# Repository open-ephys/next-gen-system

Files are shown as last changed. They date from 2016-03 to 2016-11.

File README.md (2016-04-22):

##  Next generation electrophysiology acquisition core
This repository is a work in progress repository for next generation open
source acquisition and closed-loop feedback system for multichannel
electrophysiology.

This project will hopefully end up being more than just an [open
ephys](http://www.open-ephys.org/) associated standard and will possibly be
moved to a different host org. Ideally we could end up with a set of open, and
evolving interface standards, code blocks and APIs that many different projects
can adapt parts of.

See the [working draft of the
specification](https://open-ephys.atlassian.net/wiki/display/OEW/PCIe+acquisition+board)
for details on the projects goals and desired features.

For now, we are aiming to build a working proof-of-principle prototype that we
can use as starting point to develop proper standards.

## License

### Hardware

<br/>
<span
    xmlns:dct="http://purl.org/dc/terms/" property="dct:title">Open Ephys FMC Intan IO module
</span> 
by 
<a xmlns:cc="http://creativecommons.org/ns#"
href="https://github.com/open-ephys/next-gen-system/" property="cc:attributionName"
rel="cc:attributionURL">Jonathan P. Newman, Jakob Voigts</a> 
is licensed under a
<a rel="license" href="http://creativecommons.org/licenses/by-sa/4.0/">Creative
Commons Attribution-ShareAlike 4.0 International
License</a>.
<br/>
Based on a work at <a xmlns:dct="http://purl.org/dc/terms/"
href="https://github.com/open-ephys/next-gen-system"
rel="dct:source">https://github.com/open-ephys/next-gen-system </a>

### Software
To be decided. Will likely be different licences for different layers of the
system (e.g. the firmware and devices drivers versus APIs and language bindings
versus plugins for various applications).

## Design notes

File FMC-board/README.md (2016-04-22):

# FMC Daughter Board

### Documentation

This board roughly conforms to the VITA 57 standard for LPC (low pin count) FMCs (FPGA Mezzanine Card).

It contains:
- 3x direct SMA connectors to the fpga, with overvoltage diode protection.
- 2x intan compatible 12pin omnetics connectors (A & B) for the intan headstage SPI standard, wired directly to the fpga, with a power supply.
- 1x isolated intan compatible connector (C) isolated through LVDS to CMOS converters and galvanic isolators. This headstage has its own power supply that is fed through am isolated DC-DC converter.
- 3x directional SMA connectors (on the card front edge) that are routed through the same isolation circuit as headstage connector C

The overall proposed architecture of the system is outlined [here](https://open-ephys.atlassian.net/wiki/display/OEW/PCIe+acquisition+board)

### Pinout
FMC LPC pinout can be found [here](https://docs.google.com/spreadsheets/d/18WfmbLGt8bGUUdksKp6AKA_wMX2SJ3Tndin-nnEgUCs/edit#gid=584734392)

### BOM
The bill of materials for this device can be found
[here](https://docs.google.com/spreadsheets/d/18WfmbLGt8bGUUdksKp6AKA_wMX2SJ3Tndin-nnEgUCs/edit?usp=sharing).

## Manufacturing requirements
- 4 layers
- 8mil trace width & spacing
- 12mil min. drill

There is one 0.05" pitch BGA connector (the samtech FMC connector) and a few omnetics connectors with inacessible pins on the board, so a stencil and reflow soldering need to be used.

The samtech FMC connector might need to be clamped or held down during reflow soldering. The samtec docs state that they should settle on their own during reflow though, so trying that first seems like a good idea (  http://suddendocs.samtec.com/processing/searay_soldering1.pdf ).

There is a round pad of kapton tape on the connector to provide a clamping surface for this purpose. We have had good success with using a steel paperclip that we modified to exert less force by cutting two slots into the spring. The original paper clips push down too hard and can warp the conenctor. Possibly just weighting it down with a suitable object could also work. Finally, the size of the connector means that it heats up pretty slowly, so expect it to reflow after everything else on the board, and if possible use proper pre-heating.

In order to meet approximately correct trace impedances, the design further is assuming:
 - 1oz copper
 - ~1.2mm total board height, ~0.25mm per layer, dielectric ER = 4.5

## TODO (Rev 1.0)
- [ ] Instead of conforming to VITA 57, PCB footprint should be made to fit in
  a PC expansion slot and be connected to the KC705 using a flex [FMC
  cable](http://suddendocs.samtec.com/prints/hdr-169472-xx-mkt.pdf). This will
  modularize the IO modules, potentially creating an ecosystem of different
  modules for different applications. It will also use extremely standardized
  interface (rear PC expansion slots) which also have excellent
  electrical/mechanical characteristics.
    - A couple interesting IO Module ideas
        - Analog module (e.g. NI DAQ replacement with some beefy multiplex SAR
          ADC and DAC on it)
        - Isolated Intan module (Similar to existing design, featuring galvanic
          isolation)
        - Adjustable logic level digital IO module
        - SPI compression module
        - Etc...
- [ ] As per [page 24 of the KC705 user
  guide](http://www.xilinx.com/support/documentation/boards_and_kits/kc705/ug810_KC705_Eval_Bd.pdf)
  we need to jumper the TDI and TDO pins of our FMC connectors to allow pass
  through of JTAG signals so the FPGA can be programmed when the FMC module is
  connected.
- [ ] For galvanically isolated IO module, we should conform to human use
  standards. Jakob has some info on what is required for this.

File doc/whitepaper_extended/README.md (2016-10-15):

# Open Instruments Whitepaper Extended version,

__Note:__ Contains interface specification overview and progress report.

## Overview

This whitepaper outlines an instrumentation system for neuroscience (and other
fields) that makes full use of existing technologies and industry standards to
deliver the ver high performance levels and modular design. The system can be
used as a platform for existing and future data sources, reducing development
overhead, while providing increases in system performance performance and
interoperability. This will also result in extendability to future interface
technology generations without the need for device specific re-engineering.

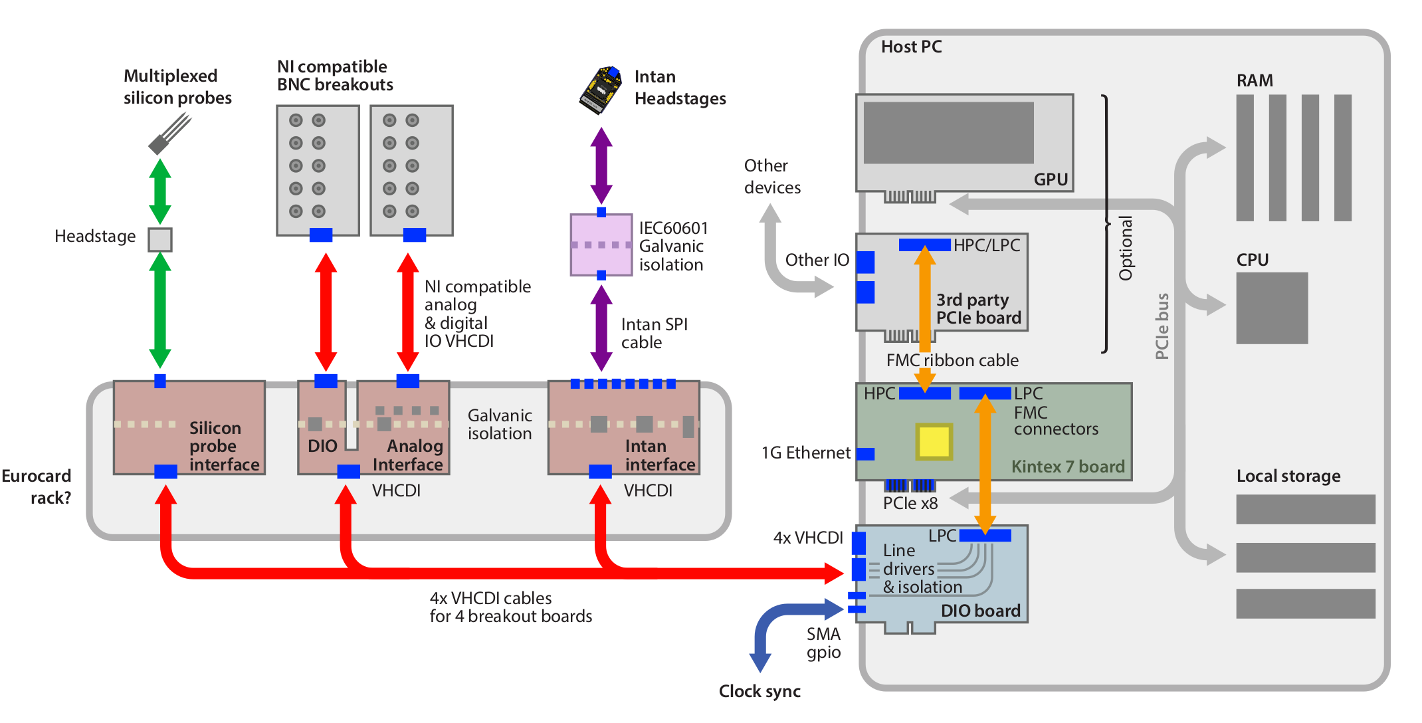
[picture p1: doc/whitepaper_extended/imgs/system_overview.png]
Example hardware configuration of a Open Instruments system with three connected breakout boards. In addition to the DIO board that provides the electrical connections between the FPGA and the breakout boards, a 3rd party FMC board is shown, connected to the FPGA through the second FMC connector.


_Example hardware configuration of a Open Instruments system with three
connected breakout boards. In addition to the DIO board that provides the
electrical connections between the FPGA and the breakout boards, a 3rd party
FMC board is shown, connected to the FPGA through the second FMC connector._

We have built a prototype system based on parts of these specifications that
delivers full use of the PCIe bus (12 Gbps throughput currently, up to 100 Gbps
with other FPGA boards). This provides adequate bandwidth for above 10,000
channels sampled at 30 kHz, and low latency of less than 100 μs round trip
between the host PC's main RAM allowing high level languages and libraries to
be used for closed-loop experiments. The same system potentially could also be
used for dynamic clamp applications using a real-time OS, delivering less than
10 μs loop capability.

The __Open Instruments__ standard does not specify or constrain the design of
either the data sources, nor the software used for data acquisition, but
specifies a flexible interconnect between the two. 

To implement a system based on new type of probe, only two or three components
need to be designed: 

  1. A hardware interface that connects directly to FPGA pins trough a
     standardized high-speed digital interconnect via generic 68-pin VHDCI
     connectors and cables that are connected to the FPGA boards via the
     ubiquitous FMC connectors and an intermediate DIO board as mechanical
     interconnect.
  1. A firmware module for the FPGA that drives this hardware, but does not
     need to be able to communicate with the host PC, or be developed with
     drivers in mind.
  1. (Optional) A software that communicates with this hardware through the
     open instruments AI that provides a generic interface to the hardware via
     data transfers and device registers, and can be used with no knowledge of
     the underlying interconnect (PCIe, USB, Ethernet).

By removing and standardizing the intermediate components of hardware-software
interfaces, the development effort required for this is vastly reduced, and
different data sources can be operated together in one system.

## Progress & Proof of Principle

The main design constraints behind this specification are high throughput and
low latency. In terms of throughput, most current interfaces can achieve or
exceed 10 Gbs. [PCIe](https://en.wikipedia.org/wiki/PCI_Express), which is used
as the basic for almost all other existing interfaces can currently achieve
around ~100 Gbs, which far exceeds the bandwidth required for any current or
mid-term electrophysiology applications, but could be useful eventually. By
contrast, latency varies widely across interfaces, and PCIe can achieve far
shorter closed-loop delays than any other mainstream interface for commodity
PCs.

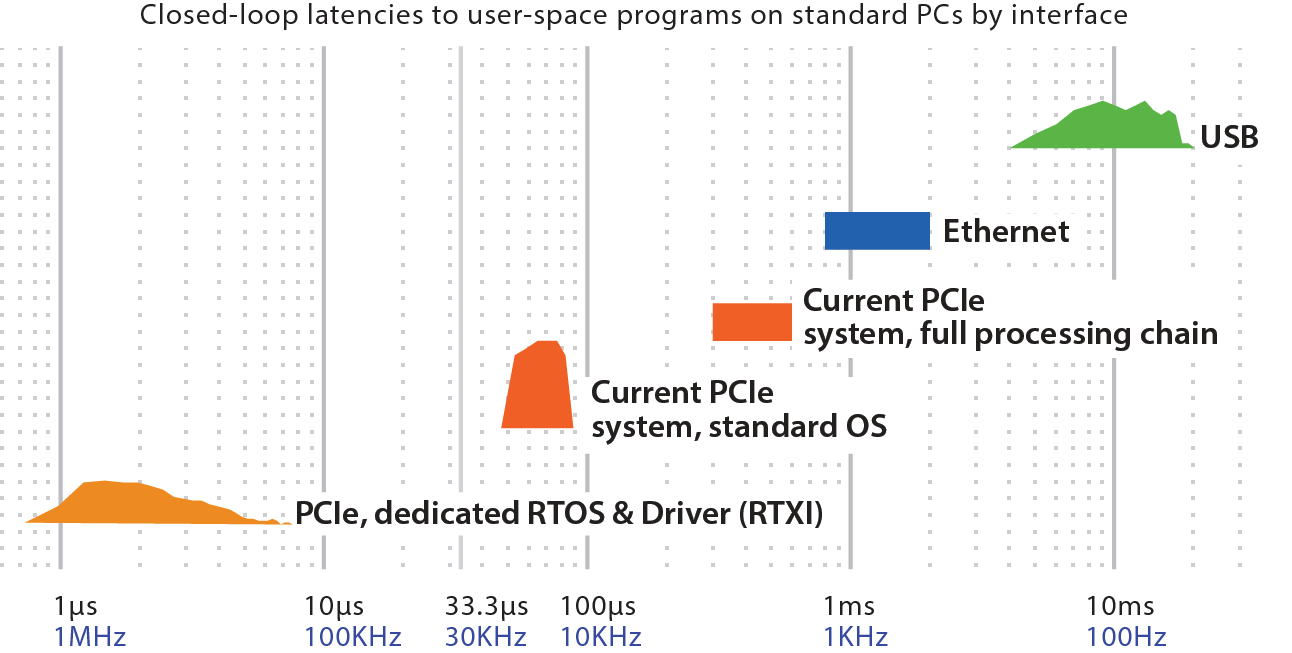
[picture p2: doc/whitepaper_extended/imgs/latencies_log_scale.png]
Overview of latencies across hardware interfaces. Histograms reflect measured latencies, bar plots reflect estimates.


_Overview of latencies across hardware interfaces. Histograms reflect measured
latencies, bar plots reflect estimates._

We have designed a prototype system based on a PCIe FPGA evaluation card
(latency measurements are shown above) and used it to verify the feasibility of
low-latency feedback on commodity PC hardware. 

In addition to verifying the feasibility of low-latency feedback via PCIe, we
tested the computational tractability of closed-loop experiments on a commodity
PC. By performing low-latency computations in a separate real-time thread, we
were able to detect spikes and perform significant additional computations on
each of 512 channels while reacting to spikes in less than 100 μs.

## Specification Overview

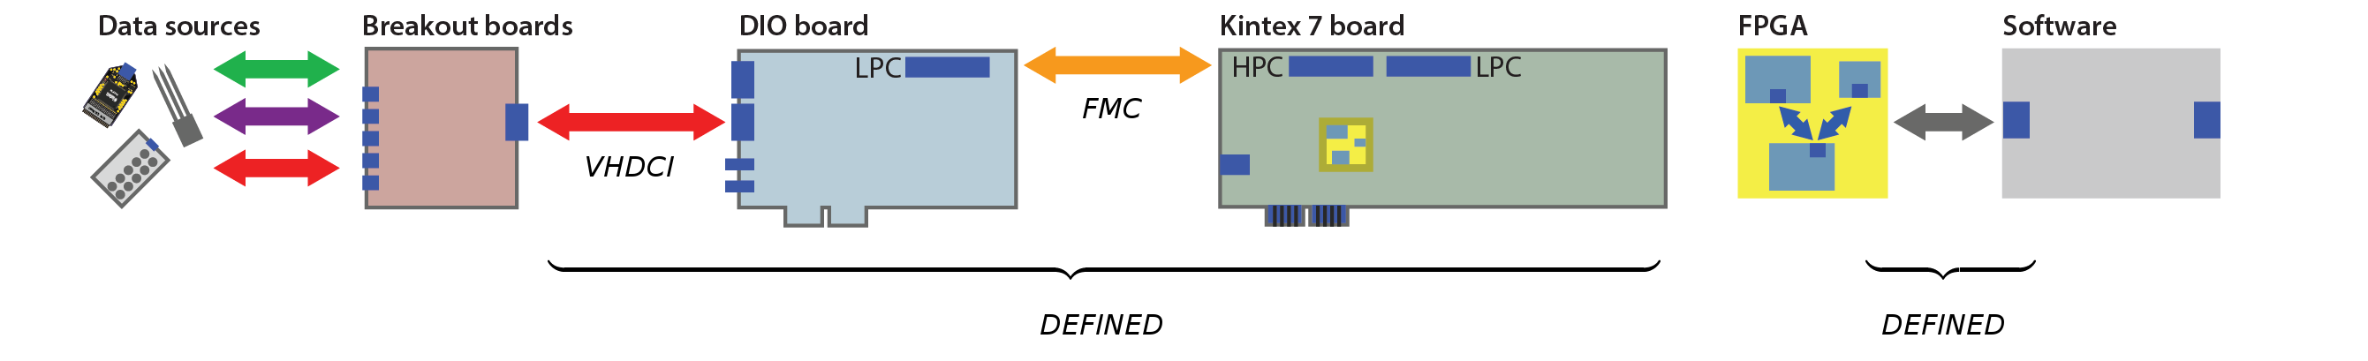
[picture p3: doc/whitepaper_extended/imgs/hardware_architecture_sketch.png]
Overview of the components and interfaces of the system. Only the interconnect infrastructure between the data source and the software are defined by the open instruments standard.


_Overview of the components and interfaces of the system. Only the interconnect
infrastructure between the data source and the software are defined by the open
instruments standard._

### Interface for Hardware Modules

This specification does not apply any constraints to the data source other than
the presence of a standardized VHDCI connector. This makes it possible for
almost any hardware to integrate into the system with minimal engineering
effort, and without sacrifices in performance.

Most pins on the cable are connected directly to the FPGA, arranged in the
following manner

  - 21 LVDS pairs that can be used in any way (including as 42 non-LVDS
    signals, depending on the device-specific firmware). 
  - 2 pins are dedicated to an I2C bus to obtain daughter board IO IDs and
    metadata,
  - 4 undefined pins for that can be used in any way
  - 20 Power supply pins (12 ground pins, 4 +5V pins, and 4 +12V pins) ground
    and VCC. 

See google [doc of pin out specification] (https://docs.google.com/spreadsheets/d/18WfmbLGt8bGUUdksKp6AKA_wMX2SJ3Tndin-nnEgUCs/edit#gid=438515320)

VHDCI cables are very widely available in low cost or very high quality
variants, and are very robust and rated for many cycles. Examples of hardware
modules are:

  - A simple Analog/Digital front-end with ADCs DACs and line receivers and
    drivers for digital input/output. This would also be the only piece of
    hardware needed to use the system in a dynamic clamp whole-cell experiment.
  - An interface to Intan headstages.
  - A digital interface connecting to high density CMOS probes.

### Hardware: DIO Card & FPGA Evaluation Card

There are only two hardware components of the system that are defined by this
specification:

  - An off-the shelf FPGA eval board (Kintex 7). This board hosts the FPGA that
    holds the device-specific firmware, as well as a piece of firmware that
    connects to the software, via the open instruments API. Exchanging this
    board for other FPGA carrier boards is relatively simple because we use
    industry standard FMC connectors to connect to the DIO board.
  - A very simple DIO card that directly connects pins on the FPGA to
    connnectors on the back of the host PC (via a FMC connector on the FPGA
    carrier board). The main role of this card is to provide direct electrical
    access to the pins of the FPGA. The FPGA pins on the FMC connector are
    broken out into 4 VHDCI connectors.

### Interfaces for Firmware Module

The open instruments standard does not specify the firmware / IP cores used to
interact with specific data sources. It does however provide a standardized
interface to a piece of firmware / IP core on the FPGA that provides a
flexible, bidirectional interconnect to the software. This minimizes
development efforts for new data sources by eliminating the redundant task of
driver and API development.

Examples of data source specific IP are:

  - An Analog/Digital IO driver that connects to a Analog/Digital front-end,
    handling the ADCs etc.
  - An Intan firmware IP core that replicates the existing Intan Rhythm
    firmware. 
  - A generic SPI interface module that can connect to data sources that
    already include an FPGA that can implement an SPI interconnect. This could
    for instance allow electrophysiology systems to be extended with very low
    latency capability.

### Software Interface

This specification does not impose any limitations on the software used to
operate the hardware modules, but specifies a very flexible interface by which
the software communicates with the hardware. This means that both the IP cores
and the software can be independent of the actual interconnect implementation.

Every communication between the software and the hardware can be cast as either
_(i)_ a read or write from/to a register (of arbitrary size) on the hardware,
for example for configurations, state read-outs etc. or _(ii)_ a read or write
from/to one of possibly many streams, for example for neural data or control
signal streaming.

The API also specifies how devices connected to the FPGA can be discovered and
identified by software, and keeps track of connection status.

## Next steps

Even though we have developed most of the specification and implemented a
working prototype system, there are a number of tasks that we will need to
complete in order to make the system practically functional and usable by other
developers:

  - Design and fabricate the DIO card to interface hardware modules to the
    FPGA.
  - We will also develop two very simple core hardware modules: An Intan
    amplifier chip interface identical to current basic intan systems, and an
    Analog/Digital front-end.
  - Implement the open instruments API around an existing PCIe firmware and
    driver, possibly using the existing xillybus driver as a short-term
    solution, and port some existing software packages (Bonsai, Open Ephys) to
    use the API to acquire neural data.
  - Implement the generic digital interconnect to commercial systems and
    implement some basic data streaming functionality.
  - We will need to move the PCIe interface to a firmware and driver that do not impose licensing restrictions. This is especially important for use of the system as component of commercial systems.

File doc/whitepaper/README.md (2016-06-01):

# Open Instruments Whitepaper

This whitepaper outlines an instrumentation system for neuroscience (and other fields) that makes full use of existing technologies and industry standards (PCIe and FMC connectors) to deliver the highest possible performance and modularity. The system can be used as a platform for any existing and future data sources, reducing development overhead, without imposing any performance or usability drawbacks. This also result in extendability to future interface technology generations without the need for device specific re-engineering.

Example hardware configuration of a Open Instruments system with three connected data source 'breakout boards'. In addition to the DIO board that provides direct electrical connections between the FPGA and the breakout boards, a 3rd party FMC board is shown, connected directly to the FPGA through t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

_Example hardware configuration of a Open Instruments system with three connected data source 'breakout boards'. In addition to the DIO board that provides direct electrical connections between the FPGA and the breakout boards, a 3rd party FMC board is shown, connected directly to the FPGA through the second FMC connector._

We have built a prototype of the system that delivers full use of the PCIe bus (12Gbps throughput currently, up to 100Gbps with other FPGA boards) for >10.000 channels sampled at 30kHz, and low latency of  <100μs round trip to and from the host PC, so that high level languages and libraries can be used for closed-loop experiments. The same system could also be used for dynamic clamp applications using a real-time OS, adding <10μs closed loop capability to existing and novel amplifier systems.

The open instruments standard does not specify or constrain the design of either the data sources, nor the software used for data acquisition, but specifies a flexible interconnect between the two. 

To implement a system based on a new type of data source, only two or three components need to be designed: 

(__1__) A hardware interface that connects to the data source and to FPGA pins on the open instruments board directly through a standardized high-speed digital interconnect via generic VHDCI connectors and via the ubiquitous FMC connectors and an intermediate DIO board as mechanical interconnect.

(__2__) A firmware module for the FPGA that drives the hardware (via any interface standard directly trough FPGA pins), but does not need to be able to interface with the host PC, or be developed with specific drivers in mind.

(__3__, optional) Data-source specific software that communicates with the hardware through the open instruments API which provides a generic interface to the hardware via data transfers and device registers, and can be used with no knowledge of the underlying interconnect (PCIe, USB, or Ethernet).

 By removing and standardizing the intermediate components of hardware-software interfaces, the development effort required for this is vastly reduced, and different data sources can be operated together in one system.

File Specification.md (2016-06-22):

# Open Instruments Specification

This specification defines interfaces for instrumentation systems for
neuroscience (and other fields) that makes full use of existing technologies
and industry standards to deliver the highest possible performance levels and
modular design. The system can be used as a platform for existing and future
data sources, reducing development overhead, while providing increases in
system performance and interoperability. The standard will also result in
extendability to future interface technology generations without the need for
device specific re-engineering.

For a brief overview, see the whitepaper at https://github.com/open-ephys/next-gen-system/tree/master/doc/whitepaper_extended

## Overview

An Open Instruments compatible system consists of one or more data sources or
effectors, termed 'daughter devices', that interact with software on a PC via
a series of standardized interfaces. The Open Instruments standard does not
specify or constrain the design of either the daughter devices, nor the software
used for data acquisition, but specifies a flexible interconnect between the
two.

Example hardware configuration of a Open Instruments system with threesd connected daughter devices / breakout boards. In addition to the DIO board that provides the electrical connections between the FPGA and the breakout boards, a 3rd party FMC board is shown, connected to the FPGA through the se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

_Example hardware configuration of a Open Instruments system with three
connected daughter devices / breakout boards. In addition to the DIO board that provides the
electrical connections between the FPGA and the breakout boards, a 3rd party FMC
board is shown, connected to the FPGA through the second FMC connector._

Examples of hardware modules / daughter devices  are:

  - A simple Analog/Digital front-end with ADCs DACs and line receivers and
drivers for digital input/output. This would also be the only piece of hardware
needed to use the system in a dynamic clamp whole-cell experiment. 

- A mostly passive interface to Intan headstages, with LVDS line interfaces,
- power supplies and galvanic isolators.

- A digital interface connecting to high density CMOS probes.

To add a new type of probe to an existing open instruments system, only two or three components
need to be designed:

  1. A hardware interface that connects directly to FPGA pins through a
  standardized high-speed digital interconnect via generic 68-pin VHDCI
  connectors and cables (which are connected to the FPGA boards via 
  FMC connectors and an intermediate DIO board as mechanical interconnect). 

  1. A firmware module / IP core for the FPGA that drives this hardware, but
  does not need to be able to communicate with the host PC, or be developed
  for specific drivers.

  1. (Optional) Software that communicates with this hardware through the open
  instruments AI that provides a generic interface to the hardware via data
  transfers and device registers, and can be used with no knowledge of the
  underlying interconnect (PCIe, USB, Ethernet).

By removing and standardizing the intermediate components of hardware-software
interfaces, the development effort required for this is vastly reduced. As an
added benefit, different data sources can be operated together seamlessly in
one system.

Overview of the components and interfaces of the system. Only the interconnect infrastructure between the data source and the software are defined by the open instruments standard.

_Overview of the components and interfaces of the system. Only the interconnect
infrastructure between the data source and the software are defined by the open
instruments standard._

#### Definitions

_Daughter device_ - Physical device / breakout bard that acts as a data source, or effector.

_Device type_ - unique id (enum specified in the API) that identifies daughter device types
and specifies the IP core, and device specific API that is used.

_Port_ - A VHDCI connector that connects a daughter device to the DIO board.

_DIO board_ - A PCIe format card that provides an electrical interconnect between
the FPGA and the daughter devices.

_FPGA board_ - A PCIe board that hosts the FPGA, as well as FMC connectors.

_FMC connector_ - A high pin count standardized connector for attaching devices to
FPGAs specified in the Vita 57 standard.

_IP core_ - A piece of firmware code that can be loaded to the FPGA.

_Open Instruments API_ - an API used by other software to communicate to
daughter devices via the FPGA.

_Device specific API_ - an API that uses the Open Instruments API to interact with a daughter device.

## Daughter device - FPGA interface

Daughter devices connect to the FPGA (which either controls the daughter device,
or simply provides an interface to the host PC) by a flexible interface that does
not constrain what devices can be used, but ensures future interoperability.

### Physical and signal type specification

Daughter devices connect to the FPGA via a very simple DIO card that directly
connects pins on the FPGA to connnectors on the back of the host PC via a FMC
connector on the FPGA carrier board.

The main role of this card is to provide direct electrical access to the pins of
the FPGA. The FPGA pins on the FMC connector are broken out into 4 VHDCI
connectors.

See https://docs.google.com/spreadsheets/d/18WfmbLGt8bGUUdksKp6AKA_wMX2SJ3Tndin-nnEgUCs/edit?usp=sharing 
for the full pin assignment.

Most pins on the cable are connected directly to the FPGA, arranged in the
following manner

  - 21 LVDS pairs that can be used in any way (including as 42 non-LVDS signals,
depending on the device-specific firmware).    

- 2 pins are dedicated to an I2C
bus to obtain daughter board IO IDs and metadata,   

- 4 undefined pins 
that can be used in any way   

- 20 Power supply pins (12 ground pins, 4 +5V
pins, and 4 +12V pins) ground and VCC.

VHDCI cables are very widely available at low cost or in very high quality
variants, and are very robust and rated for many mating cycles.

In addition to the VHDCI connectors, the DIO card also provides a few SMA connectors that can be used as clock IO to synchronize multiple systems.

_Possible later extension:_ The kc705 boards provide 4 GTX tranceivers (12Gbps
each) on the HPC FMC connector. Many other FPGA eval boards provide similar
high-speed pins. For a further expansion of the system, these pins could be
routed to external SPF or esata connector on the DIO board, providing a
significantly higher throughput option for device specific or generic digital interfaces.

### Protocol layer

The Open Instruments standard does not enforce any protocol - a daughter device
can communicate with the FPGA via the signal lines on the VHDCI connector
defined in the physical layer in any way. This includes the use of LVDS pins for
single ended signals.

The only specification, apart from the pin out, is the presence of an i2c EEPROM
(either as IC or emulated on a microcontroller or FPGA) on the daughter device
that identifies the device to the FPGA and determines what IP cores are
conencted to the device's port. This identifier is also available to software
via the API.

#### Canconical SPI protocol

If desired, a daughter device can choose to adhere to a simple standardized
protocol to stream data to and from the system via the VHDCI connector. To do
this, the device simply needs to identify (via the eeprom) as a 'canonical SPI
device'. From the point of view of the open instruments standard, this canonical
SPI protocol and the associated IP core are treated like any other daughter
device and device- specific IP core.

In this case, the canonical SPI IP core is connected to a subset of pins on the
VHDCI port.

2do: define this more.

## FPGA - host interface 

The Open Instruments standard opaquely encapsulates the FPGA/host interface so
that neither hardware, firmware nor software need to be modified significantly in
order to switch between interfaces. On the software side, the interface is
encapsulated by the Open Instruments API, and on the firmware side by the Host
interface IP core.

Overview of latencies across hardware interfaces. Histograms reflect measured latencies, bar plots reflect estimates.

_Overview of latencies across hardware interfaces. Histograms reflect measured
latencies, bar plots reflect estimates._

### Ethernet 

Ethernet interfaces combine low latency of ~1-5ms with high
troughput of around 10Gbps on common ethernet cards, which is sufficient for
almost all current applications.

The kc705 FPGA board includes a 10gig Ethernet connector, so implementing the
interconnect via ethernet will just require an appropriate IP core.

### PCIe

[PCIe](https://en.wikipedia.org/wiki/PCI_Express), which is used as the basic
for almost all other interfaces can currently achieve throughputs of around ~100
Gbts, which far exceeds the bandwidth required for any current or mid-term
electrophysiology applications, but could be useful eventually. The most common
type of FPGA evaluation board that is recommended for open einstruments systems,
the Xilinx Kintex kc705 achieves around 12Gbps, which is sufficient for almost
all current applications.

PCIe can achieve far shorter closed-loop delays than any other mainstream
interface for commodity PCs. PCIe can achieve < 100 μs closed-loop latencies on
common operating systems, and around 1 μs on real-time operating systems (for
example, in the RTXI project).

## IP core /firmware module interfaces

The open instruments standard does not specify the firmware / IP cores used to
interact with specific data sources. It does however provide a standardized
interface to a piece of firmware / IP core on the FPGA that provides a flexible,
bidirectional interconnect to the software. This minimizes development efforts
for new data sources by eliminating the redundant task of driver and API
development.

### Wishbone bus

Individual IP cores on the FPGA communicate via a standardized interconnect
based on the wishbone specification.

2do: specify this more - ideally the wishbone specifications should very closely
mirror the API, similarly to how xillybus and opalkelly have equivalent API
calls for register writes/reads/wires to registers, and pipes/streams to fifos.

### I2C EEPROM interface

Each daughter device must contain an EEPROM on the i2c bus of the VHDCI port
that identifies the daughter device to the system. The device is identified by a
simple device id that is specified by an enum (oiDeviceType) in the open
instruments API. New device types will be appended to this enum later.

The device type fullfils two roles:

1. Specify the type of daughter device specific IP core that is connected to the port that the device is connected to. In some cases, if the required IP core is not present on the FPGA, this could require a reconfiguration of the FPGA.

1. Allow the  API to enumerate the connected devices and their types, so that an appropriate device specific API/library can be loaded.

2do: specify details

### Interconnect matrix

Each daughter device connected to one of the ports needs to be routed to an
appropriate IP core.  This is accomplished by an interconnect matrix that pairs
the pins on the port (VHDCI connector, connected to the FPGA via the FMC
connector) to nets of the appropriate IP core.

This interconnect matrix is fullly transparent to both the daughter device and
the device specific IP core, and connects all pins on the VHDCI port to
corresponding nets on the device specific IP core.

2do: when is this done? on oiOpenPort()?

### Daughter device specific IP cores

Each daughter device specific IP core is specific to one device type, defined by
the device type id enum (oiDeviceType).

In some cases, multiple instances of these cores will be implemented on the
FPGA.  For instance multiple generic SPI interfaces will likely be used
simultaneously.

The presence of a matching IP core is checked by oiGetDeviceType, and the VHDCI
pins on the port are associated with the ip core in oiOpenPort. 

2do: is oiOpenPort the correct call to do this?
2do: do we want that device specific IP cores can be enumerated by the API via
an oiGetCoreType call? 

_One possible way this could work is that we loop over the oiGetNumPorts ports,
and call oiGetDeviceType, and run oiOpenPort immediately. The return code then
signals whether an ip core is present, or present and already associated with a
port etc. Now the software could try uploading a different firmware that
includes the required IP cores?_

Examples of daughter device specific IP cores are:

  - An Analog/Digital IO driver that connects to a Analog/Digital front-end,
handling the ADCs etc. 

- An Intan firmware IP core that replicates the existing
Intan Rhythm     firmware.    

- A generic SPI interface module that can connect
to data sources that already include an FPGA that can implement an SPI
interconnect. This could for instance allow electrophysiology systems to be
extended with very low latency capability.

### Host interface IP core

All communication to the API and to device specific and user-facing software is
encapsulated on the firmware side into host interface IP cores that adhere to
the same wishbone interface as daughter device specific IP cores.

There are two types of interfaces by which the host  interface IP core
communicates with device specific IP cores: Registers, and streams.

Registers are accessed on the API via oiReadConfig and oiWriteConfig by simple
key/value (int) pairs. On the IP core, the configuration corresponds directly to
a register bank.

Ports can contain multiple streams, and each streams is accessed by oiReadStream
or oiWriteStream. On the IP core, these streams correspond to FIFOs.

2do: wrap this in a wishbone compatible interface.

Examples of host interface IP cores are:

- Ethernet

- PCIe via xillybus

## Software

The software comonents of a Open Instruments system can be divided into four
layers: Interface specific drivers, the Open Instruments API, the daughter device specific
libraries/APIs, and the user-facing software. Only the Open Instruments API is
specified by this standard and ensures interoperability between system
components. However, in almost all practical implementations, a driver (for
example for Ethernet, or PCIe) will already be present, so developers aiming to
integrate a new device only have to implement the device specific API and
possiby user-facing software.

Conversely, switching out the host PC interface should not require changes to the device specific code.

### Drivers

Drivers for the hardware-software interconnect are opaquely wrapped into the
open instruments API on one end, and the (wishbone bus compatible)
specification of the host- pc interface IP core on the other. This means that
developers can either develop for daughter devices without having to spend
time on the interconnect specifics, or swap interconnects without requiring
re-enginering of other system components.

Examples of interconnect drivers are:

- Ethernet driver, 

- xillybus.

2do: _possible exception to the independence of drivre/interconnect implementation_: 
it seems likely that we want to be able to (optionally)
configure the interconnect - for instance selecting block transfer sizes for a
speed thourghput tradeoff. We could specify that this is optional and of course
not driver independent, but that all API implementations should come with
default values so that no specific configuration is strictly required. Maybe
oiSetStreamAttributes already covers this? Or could there be other configuration
options that are needed in special cases?

### API

This specification does not impose any limitations on the software used to
operate the hardware modules, but specifies a very flexible interface by which
the software communicates with the hardware. This means that both the IP cores
and the software can be independent of the actual interconnect implementation.

The full API specification is found at https://github.com/open-ephys/next-gen-system/tree/master/API

Every communication between the software and the hardware can be cast as either
_(i)_ a read or write from/to a register (of arbitrary size) on the hardware,
for example for configurations, state read-outs etc. or _(ii)_ a read or write
from/to one of possibly many streams, for example for neural data or control
signal streaming.

The API also specifies how devices connected to the FPGA can be discovered and
identified by software, and keeps track of connection status.

### Daughter device specific APIs

On top of the Open Instruments API, there will be daugher-device specific functions that should not be implemented by the user-facing software
Examples of these are cable lenght calculation for the SPI bus on Intan chips, Impedance measurements, unpacking of data formats to interpretable values and timestamps, etc.

For this, a user facing software can use oiGetDeviceType to determine the correct device specific API to interact (via the Open Instruments API) with the hardware/firmware of that device.

### User-facing software

The User-facing software can either interact with the duagher device firmware directly trough the Open Instruments API, and/or an intermediate layer of a daughter device specific API.

Examples of user-facing software packages are:

- Minimalistic Open instruments data stream interface

- The Open Ephys GUI 

- Bonsai

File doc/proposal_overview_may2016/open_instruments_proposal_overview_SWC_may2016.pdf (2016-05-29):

# Next generation electrophysiology

# Interface standard proposal for very high data rate neurophysiology and low latency closed-loop experiments

SWC Workshop Next Gen (Open) Ephys: Hardware and Software May 25-26th 2016, London

## Requirements

> 1000 channels | NeuroPix, Neuroseeker, Miniscope, etc. ~10 Gbps, more later
< 1ms latency | Closed loop experiments, whole cell, etc.

## Ideally also

## Dynamic clamp capable: < 100μs closed loop latency to user sw

## Future proof, modular, not reliant on vendor specific components

# What design choices result from this?

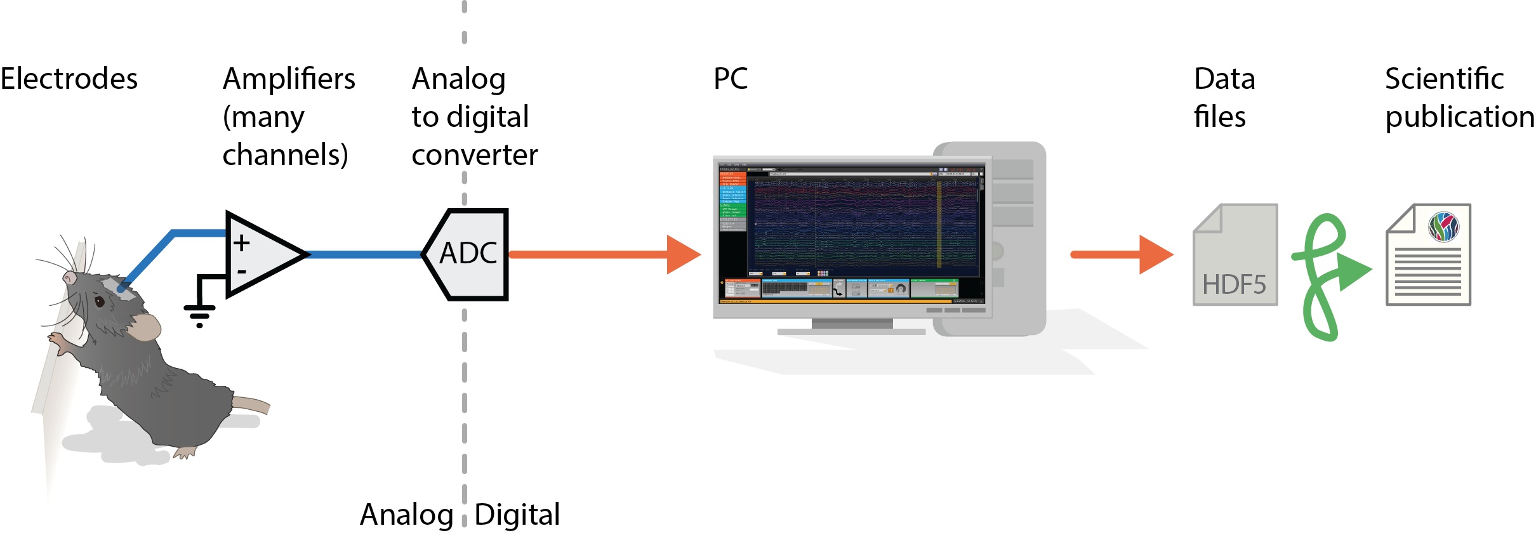
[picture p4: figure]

# Host PC interface

USB | High throughput, | High latency
| ~ 12 Gbps | ~ 15 ms
Ethernet High throughput, | Low latency
| ~12 Gbps | ~ 1ms
PCIe | Highest throughput, | Lowest latency
| ~12 Gbps (Max. ~100) | ~ 10 μs

# proof of principle: PCIe prototype

Direct PCIe DMA interface

> 1000 channels @ 30KHz
(approx. max. throughput is
25000 ch. * 16 bit * 30kHz = 12 Gb/s = 1.5 GB/s
Fills 1TB in ~11 minutes)

Aaron:
Direct port of Reid's Rhythm firmware & API via Xillybus

Jon & Jakob:
Simple FMC test board
1 isolated intan SPI connector,
1 non-isolated

3 isolated DIO (1 out, 2 in)
3 direct DIO (bidirectional)

Kintex 7 eval
PCIe 2 x4, $1600

FMC connector

# proof of principle: PCIe prototype

Kintex 7 eval
PCIe 2 x4, $1600

Intan

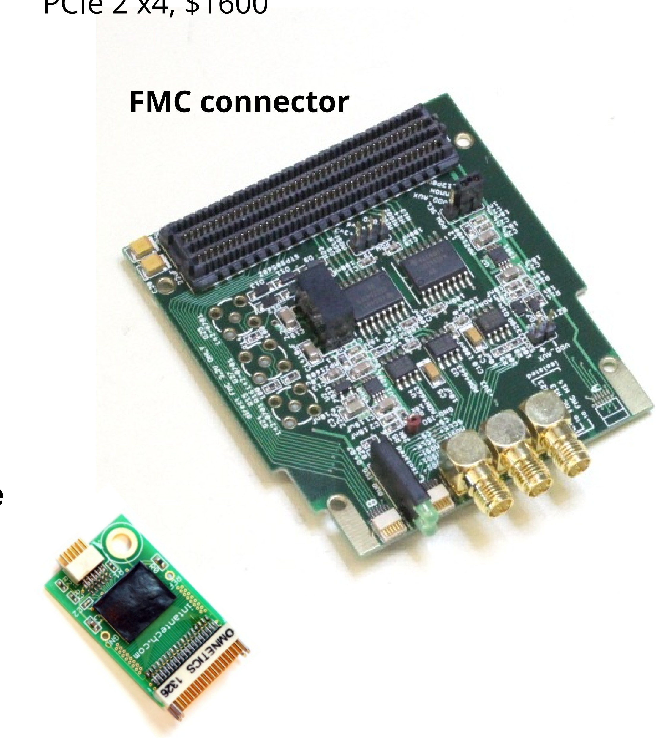
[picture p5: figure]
FMC connector

Headstage

Direct PCIe DMA interface

> 1000 channels @ 30KHz
(approx. max. throughput is
25000 ch. * 16 bit * 30kHz = 12 Gb/s = 1.5 GB/s
Fills 1TB in ~11 minutes)

Aaron:
Direct port of Reid's Rhythm firmware & API via Xillybus

Jon & Jakob:
Simple FMC test board
1 isolated intan SPI connector,
1 non-isolated

3 isolated DIO (1 out, 2 in)
3 direct DIO (bidirectional)

# PCIe prototype

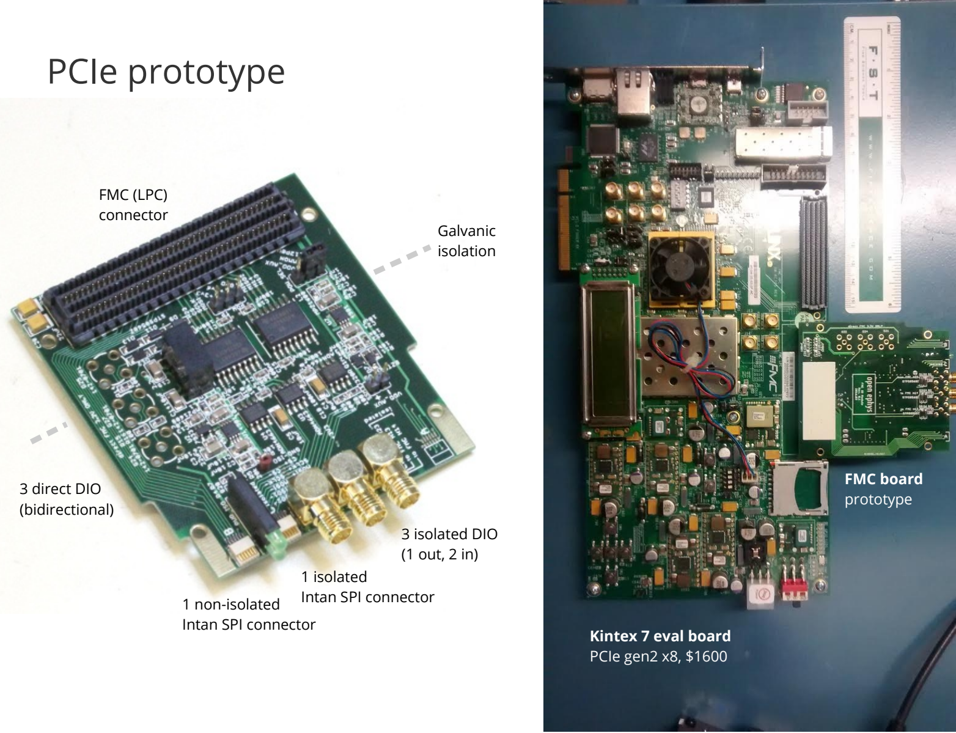
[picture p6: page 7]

Kintex 7 eval board
PCIe gen2 x8, $1600

Galvanic
isolation

3 isolated DIO
(1 out, 2 in)

3 direct DIO
(bidirectional)

1 isolated
Intan SPI connector

FMC (LPC)
connector

1 non-isolated
Intan SPI connector

FMC board
prototype

# Latency test

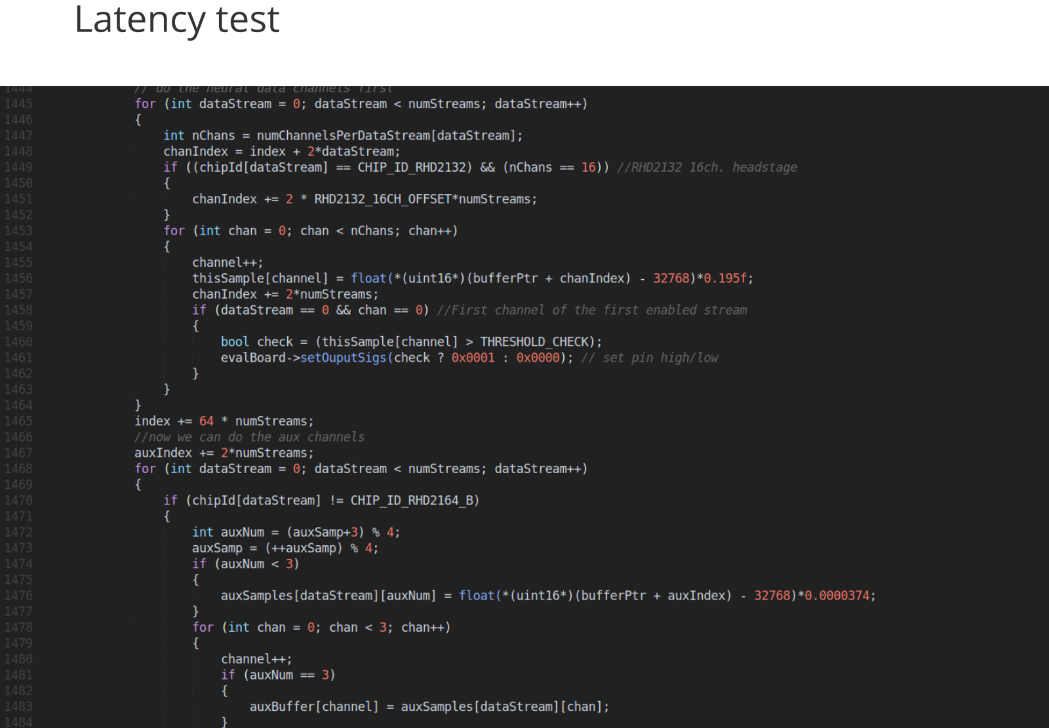
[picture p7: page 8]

# Latency test

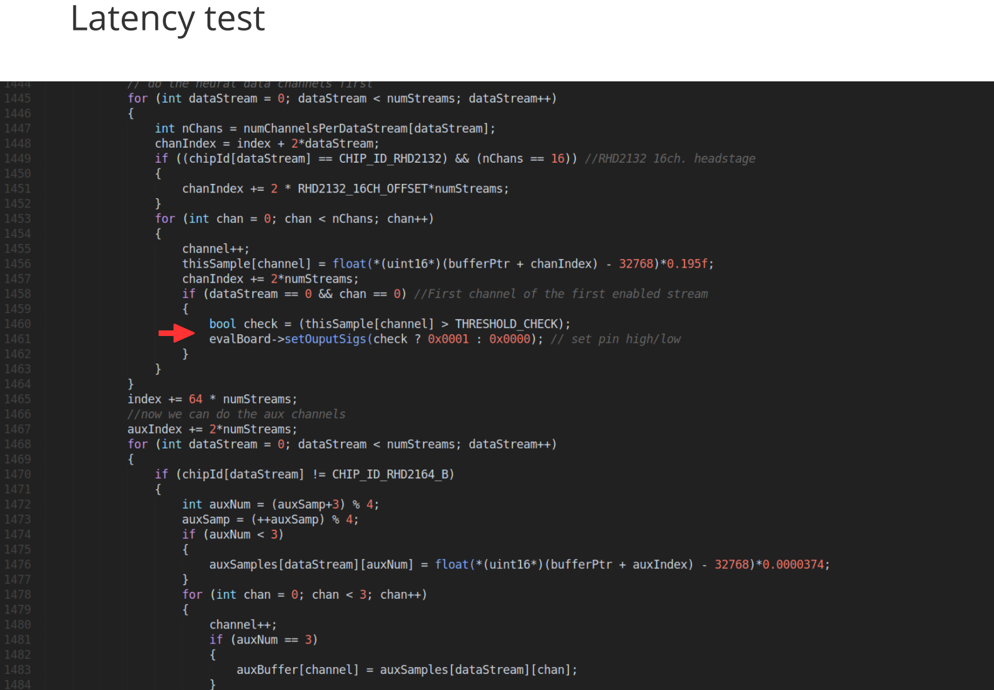
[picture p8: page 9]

# Latency test

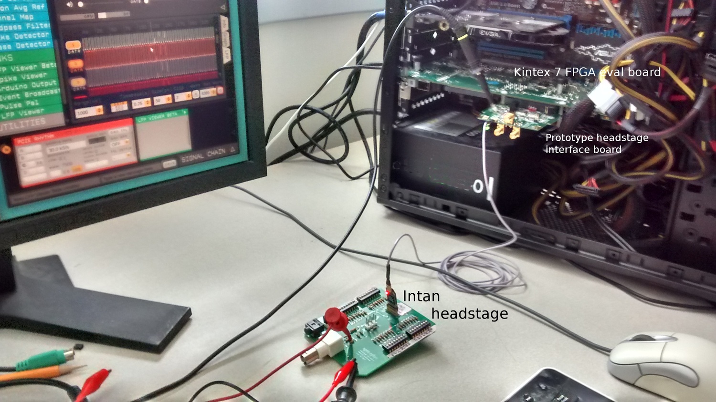
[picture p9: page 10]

# Latency results

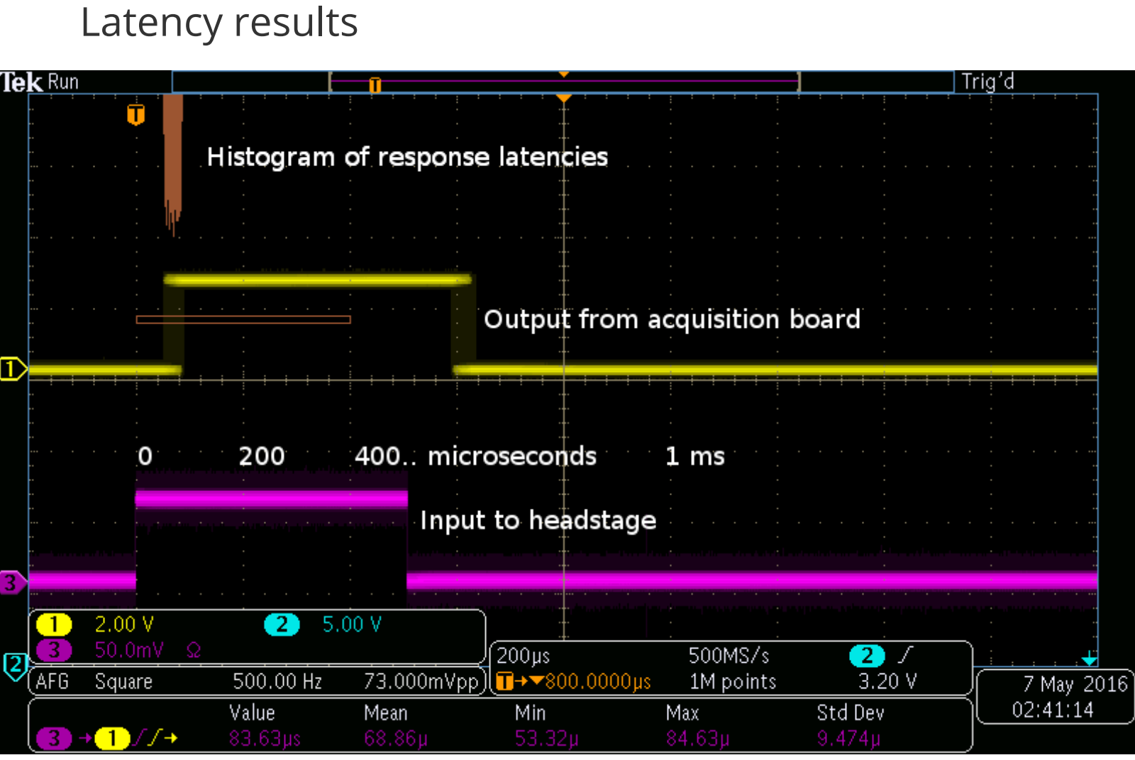
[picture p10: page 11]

# Latency results

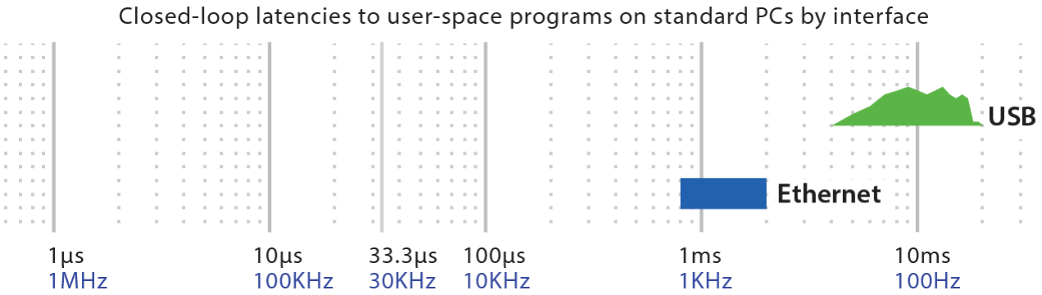
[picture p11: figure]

# Latency results

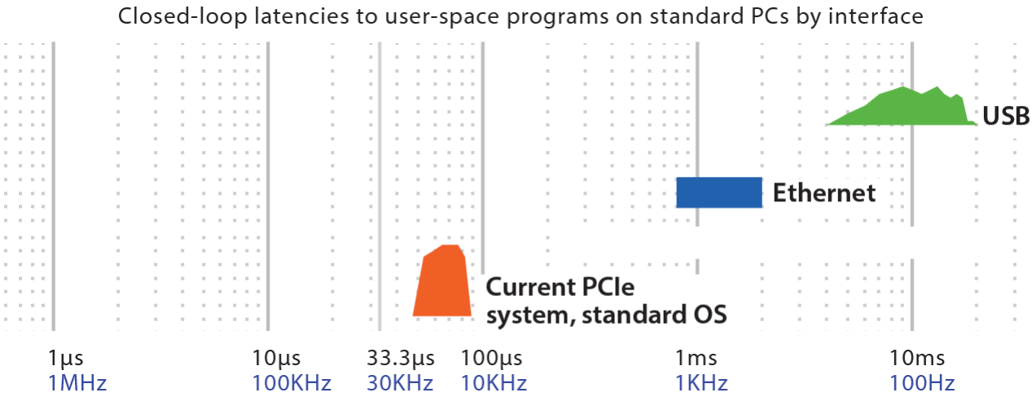
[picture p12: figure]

# Latency results

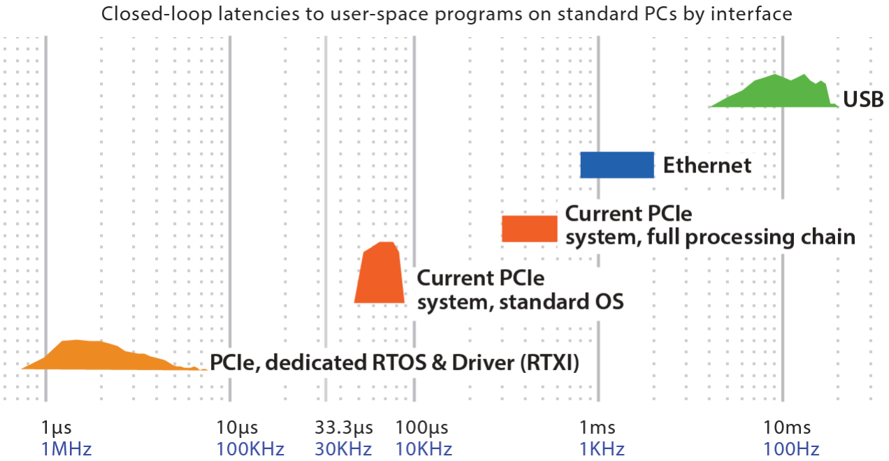
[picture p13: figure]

→ PCIe is sufficiently easy to implement,
Provides μs latency, at almost arbitrary channel counts.

# Which FPGA/PCIe card?

→ PCIe is sufficiently easy to implement,
Provides μs latency, at almost arbitrary channel counts.

# PCIe (FMC) carrier cards are already the industry standard

for similar applications.

Zynq board
ARM cortex integration

Kintex 7 eval

PCIe 2.0 x4, $1600 | HTG-828
| PCIe 3.0 x16

Cern FMC carrier
Open source design

Vadatech VPX514
VPX (VITA-46) card
(not strictly pure PCIe)

Stratix V dev kit.
PCIe 3.0 x16, dual FPGA, $15000

→ PCIe is sufficiently easy to implement,
Provides μs latency, at almost arbitrary channel counts.

# PCIe (FMC) carrier cards are already the industry standard

for similar applications.

Zynq board
Arm cortex integration

Kintex 7 eval

PCIe 2.0 x4, $1600 | HTG-828
| PCIe 3.0 x16

Cern FMC carrier
Open source design

Vadatech VPX514
VPX (VITA-46) card
(not strictly pure PCIe)

Stratix V dev kit.
PCIe 3.0 x16, dual FPGA, $15000

# Design choices for PCIe systems

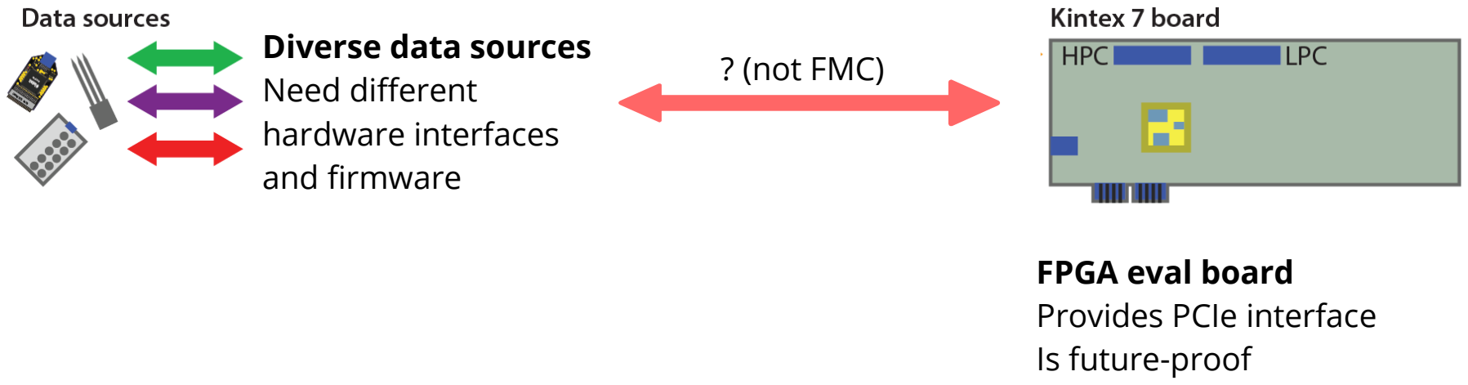
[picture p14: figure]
FPGA eval board Provides PCIe interface Is future-proof; Diverse data sources Need different hardware interfaces and firmware; ? (not FMC)

# Design choices for PCIe systems

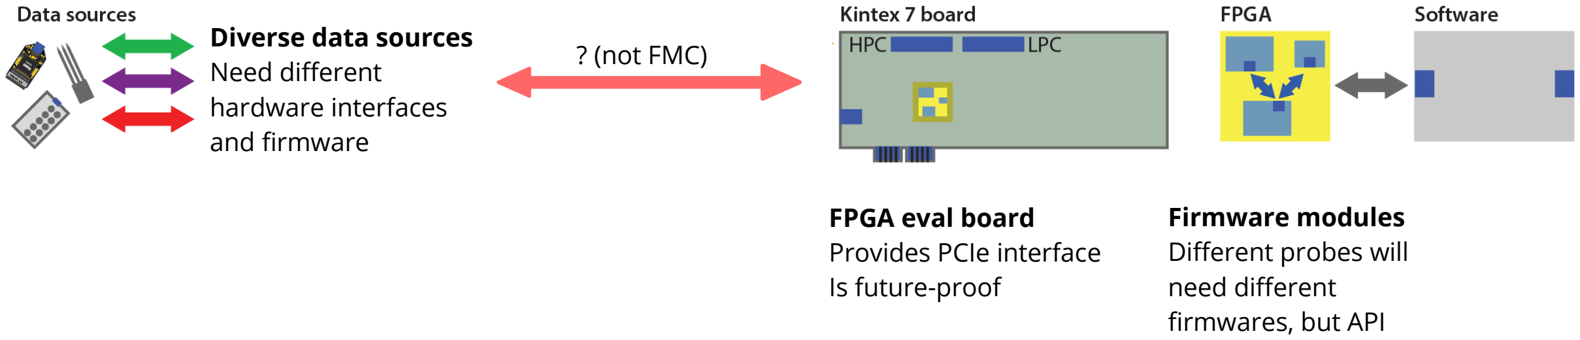
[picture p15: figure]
FPGA eval board Provides PCIe interface Is future-proof; Firmware modules Different probes will need different firmwares, but API; Diverse data sources Need different hardware interfaces and firmware; ? (not FMC)

interface can stay the
same.

# Design choices for PCIe systems

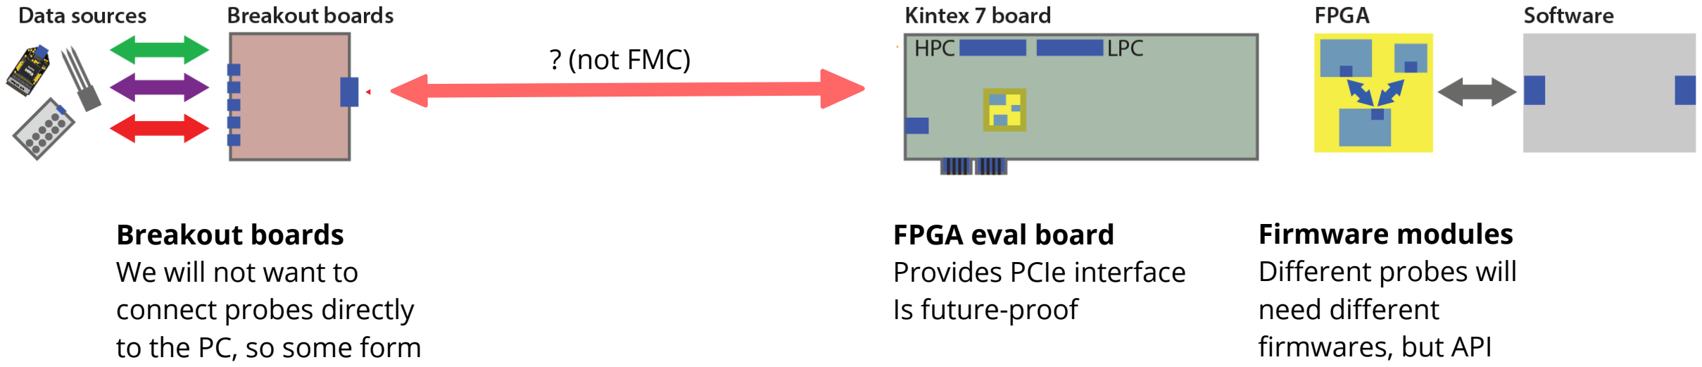
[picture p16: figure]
FPGA eval board Provides PCIe interface Is future-proof; Breakout boards We will not want to connect probes directly; Firmware modules Different probes will need different firmwares, but API; ? (not FMC)

to the PC, so some form
of breakout boards will
be needed.

interface can stay the
same.

# Design choices for PCIe systems

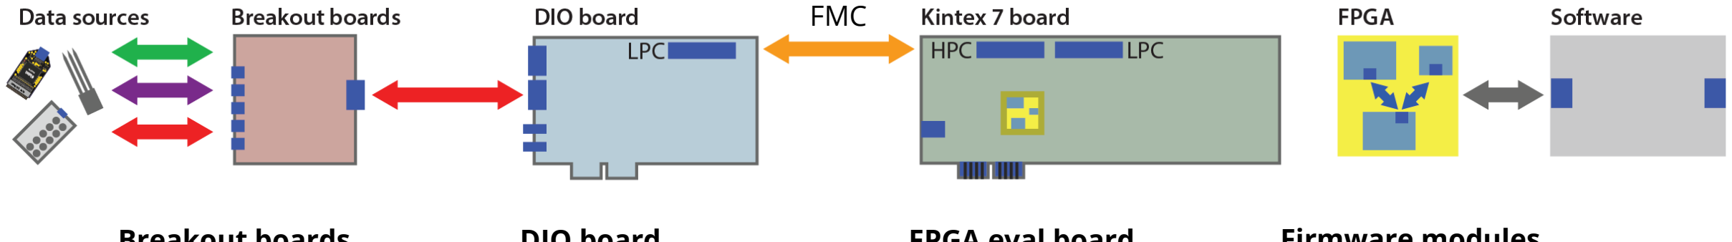
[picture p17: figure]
FMC

FPGA eval board
Provides PCIe interface
Is future-proof

Breakout boards
We will not want to
connect probes directly
to the PC, so some form
of breakout boards will
be needed.

Not always needed?

DIO board
Intermediate board
between FPGA board
and breakout boards.
FMC is great but not
useful for routing
outside PC case.

Firmware modules
Different probes will
need different
firmwares, but API
interface can stay the
same.

# Design choices for PCIe systems

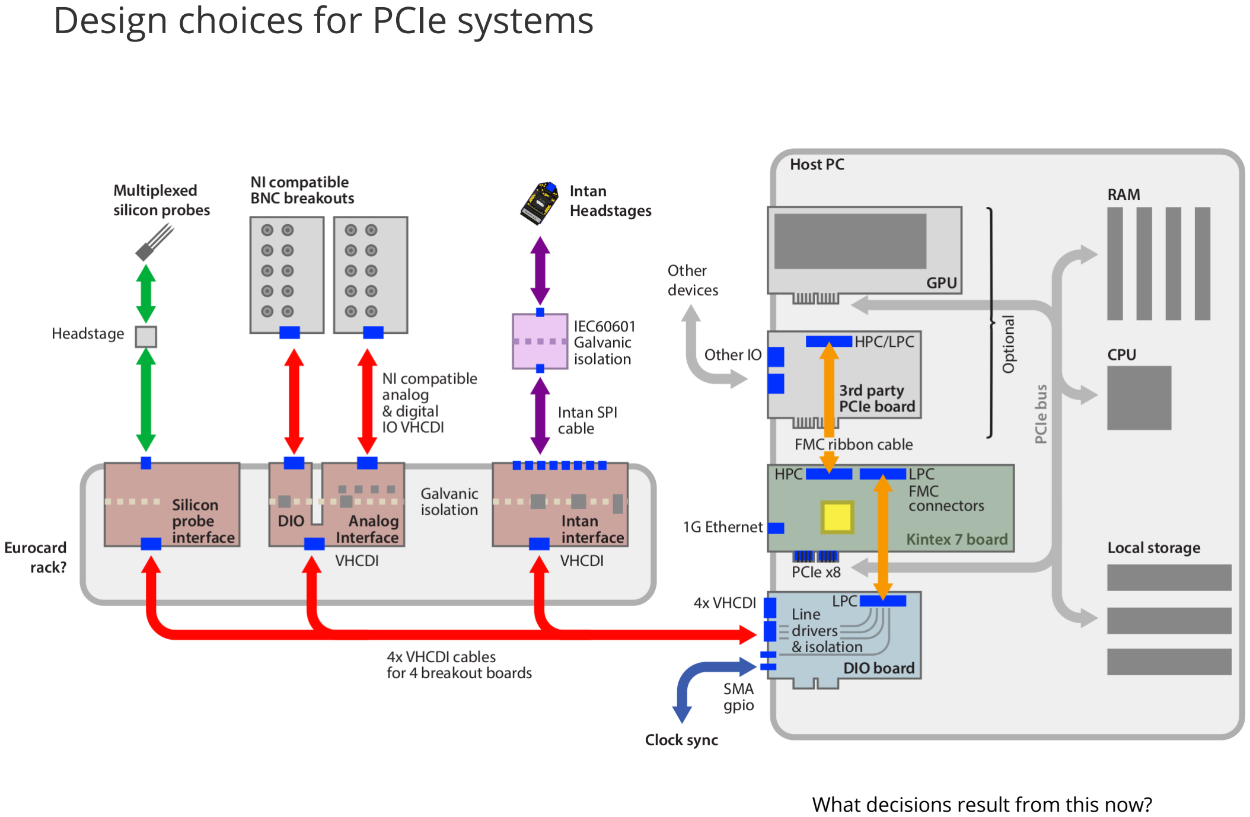
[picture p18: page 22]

What decisions result from this now?

# Design choices for PCIe systems FMC connector

To non-standard
board (microscopes etc.)

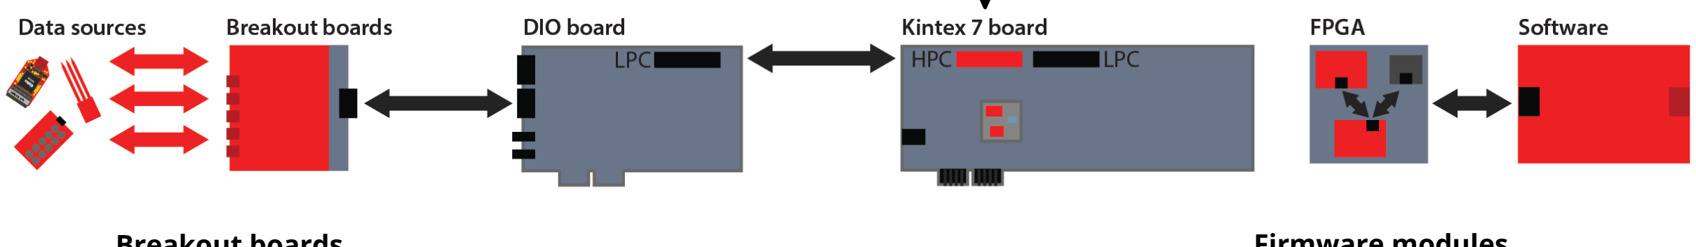
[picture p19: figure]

Breakout boards
Implement different
HW interfaces.

Firmware modules
Different probes will
need different
firmwares, but API
interface can stay the
same.

custom
standardized

# Design choices for PCIe systems

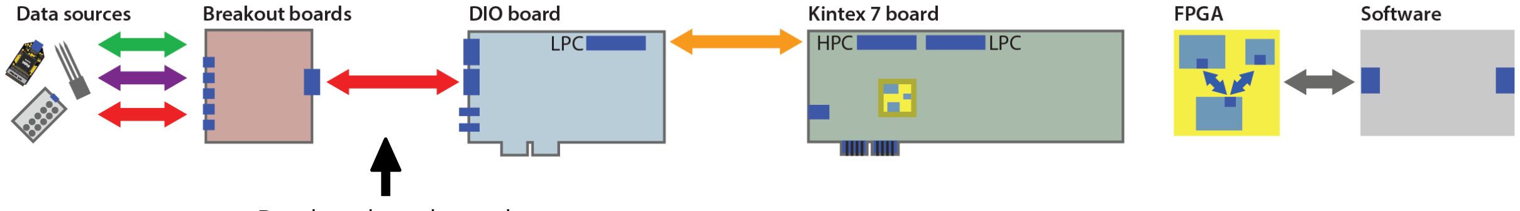
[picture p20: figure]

Breakout boards need to
connect to PC
Which connectors/cables?

# Design choices for PCIe systems

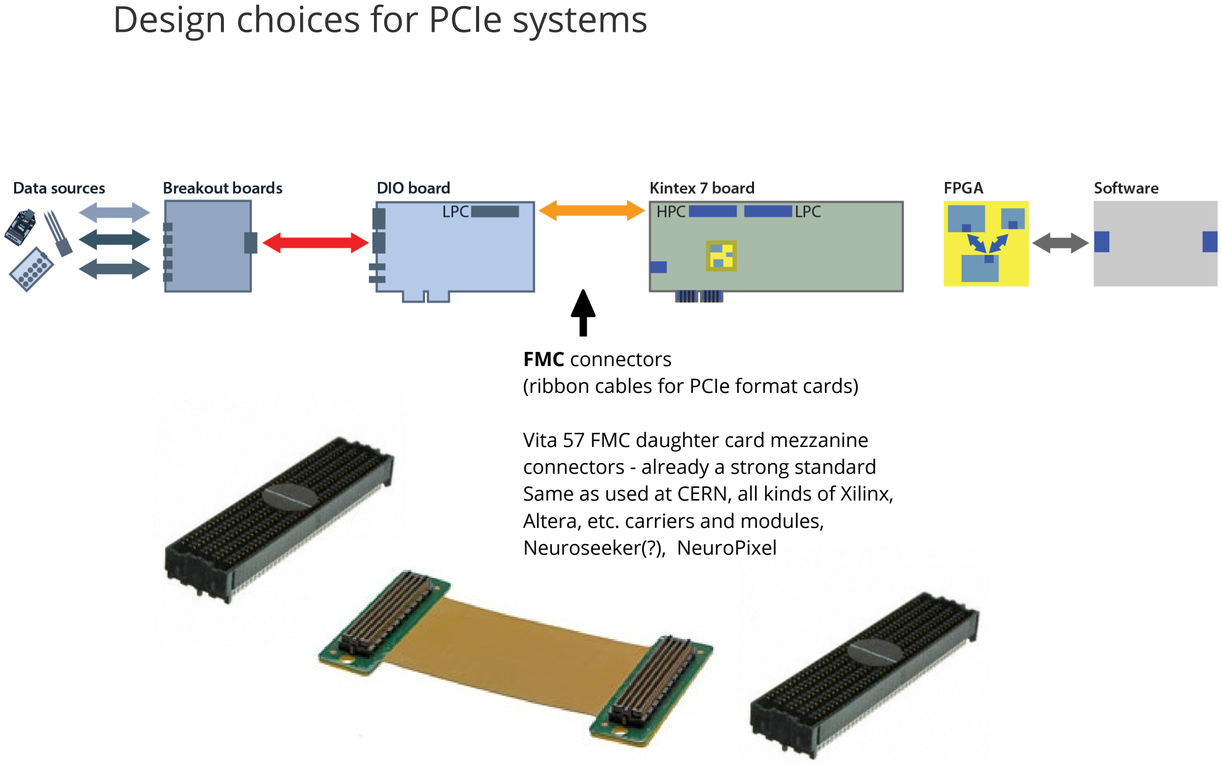
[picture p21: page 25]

FMC connectors
(ribbon cables for PCIe format cards)

Vita 57 FMC daughter card mezzanine connectors - already a strong standard Same as used at CERN, all kinds of Xilinx, Altera, etc. carriers and modules, Neuroseeker(?), NeuroPixel

# Design choices for PCIe systems

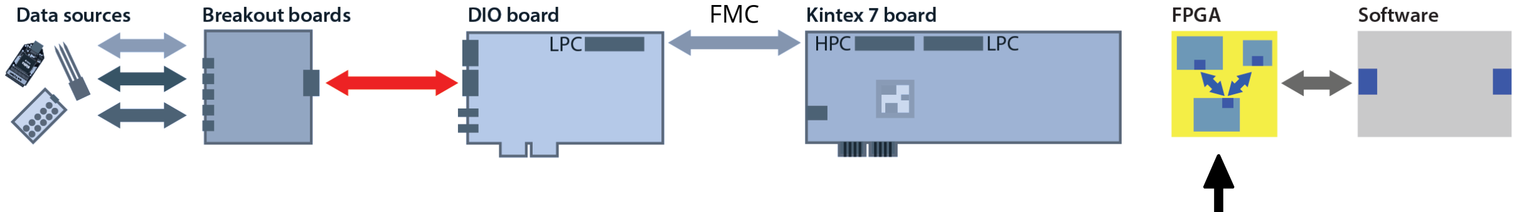
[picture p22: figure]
FMC

Firmware interconnect
Wishbone
IP cores?

# Design choices for PCIe systems

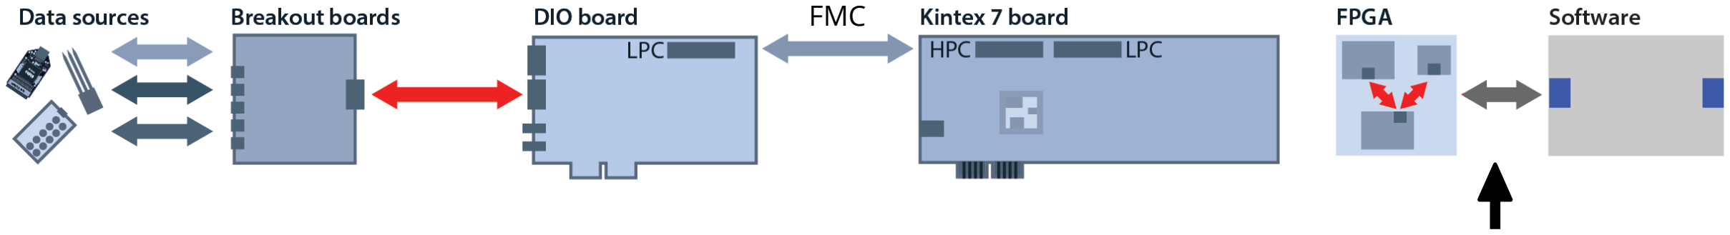
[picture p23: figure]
FMC

Host interface
PCIe (which method?)
optional Ethernet ?

# Design choices for PCIe systems

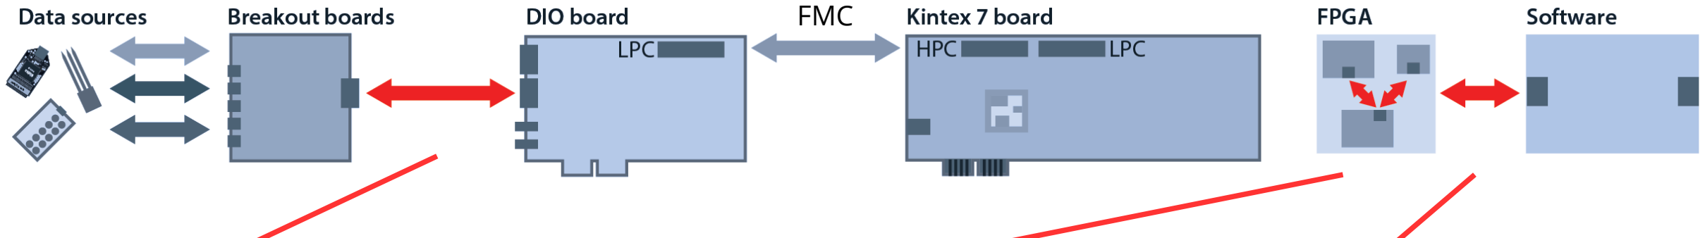
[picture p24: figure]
FMC

### 1. Breakout board

connectors

2. Firmware interconnect | 3. Host interface

# Design choices for PCIe systems


### 1. Breakout board

connectors

Just break out raw FMC pins VHCDI / SCSI cables

### 2. Firmware interconnect

Wishbone based
specification?

### 3. Host interface

Extendable PCIe based DMA
Plus ethernet for broadcast

# Breakout board connectors


Breakout board connectors

Just break out raw FMC pins to VHCDI / SCSI cables

Space for 4 conectors
& ~3 SMAs for clock etc.

68 pins
Twisted pairs
$25 - $400 options (shielded or not etc.) ~28GA ~600mA/wire →

Specify minimum number of pins
- VCC ( 3.3V & 12V ) /GND
- i2c bus for eeprom device id

Use LPC or HPC? Likely HPC since we want a decent pin count per connector.

# Breakout board format


Common use cases will employ 2-3 external breakout boards, likely double width, but there are cases for many more.

Eurocard format?

Don't use backplane, just use VHCDI? Can still use extruded aluminum case.

# Breakout board format

Common use cases will employ 2-3 external breakout boards, likely double width, but there are cases for many more.

Eurocard format?

Don't use backplane, just use VHCDI? Can still use extruded aluminum case.

Core application:
Data source Firmware
Aux input (A/D io)
PCIe interface

# IP core interfaces

Analog frontend

Intan headstages

# IP core interfaces

Extended application:
Data source Firmware
Aux input (A/D io)
PCIe interface
FPGA processing
Ethernet streaming

Analog frontend

Intan headstages

File storage server

# IP core interfaces

Interface between modules
Wishbone, which
specifications?

# IP core interfaces

Interface between modules
Wishbone interconnect?

Data format and config
register access is specified very similarly to the API.

# IP core interfaces

Host PC interface
Firmware side & Drivers

Currently use xillybus
Move to something with non-restrictive driver that can be used commercially.

# Conclusion

PCIe DMA interface is
- sufficiently developer friendly
- highest performance
- most future-proof

Proposed system can mostly use generic industry standards

Maintains compatibility with almost all existing standards

Minimizes amount of work
required for new data sources to close to theoretical minimum.

Interface specifications:
1. Breakout board standards
2. IP interconnect
3. PCIe PC interconnect ↔

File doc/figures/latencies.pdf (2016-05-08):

PCIe with very inecient but exible signal chain; Fully optimized PCIe (RTXI); Best case Ethernet; Ethernet; PCIe; PCIe on standard OS; USB 2/3; 10KHz; 1KHz

Latencies (μs) Corresponding frequencies

1KHz

100Hz

1MHz; 100KHz; 30KHz 10KHz; 1KHz; PCIe, dedicated RTOS & Driver (RTXI); Current PCIe system, standard OS; Current PCIe system, full processing chain; Ethernet; USB

Closed-loop latencies to user-space programs on standard PCs by interface

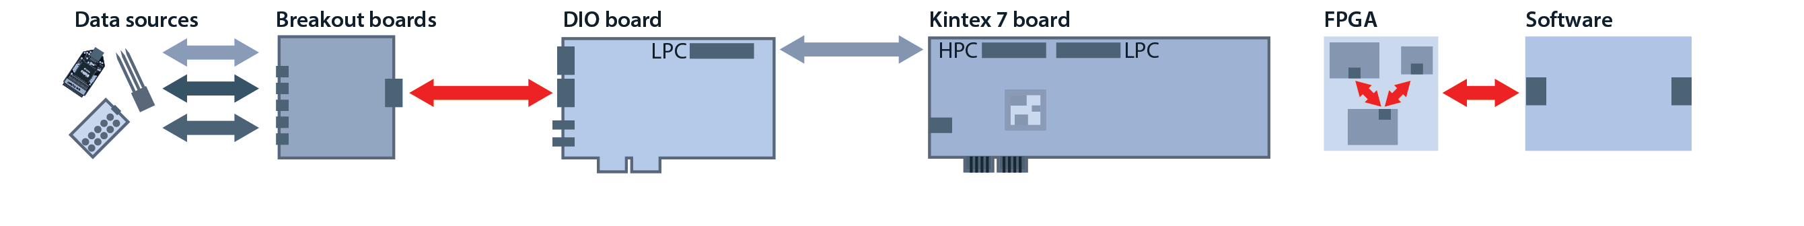
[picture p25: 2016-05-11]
doc/figures/hardware_architecture_sketch_small_highlights.png

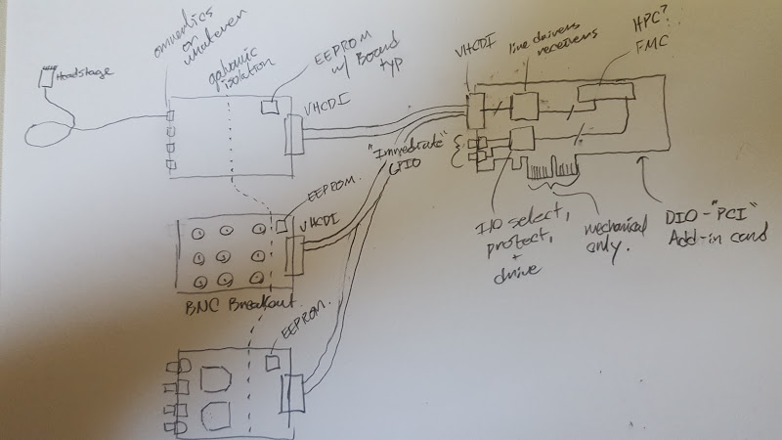
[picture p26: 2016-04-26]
pci-modules/resources/pci-breakout-concept.png

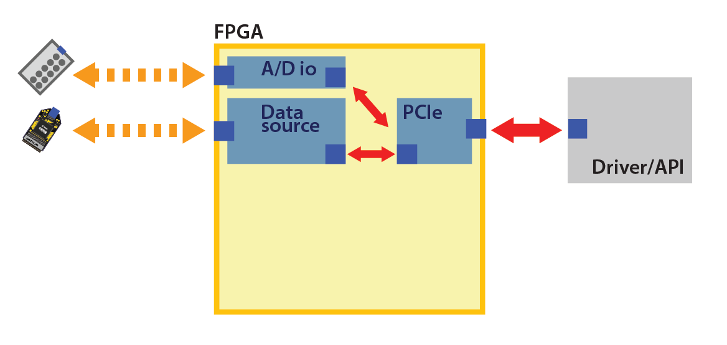
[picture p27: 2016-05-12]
doc/figures/fpga_input_only.png

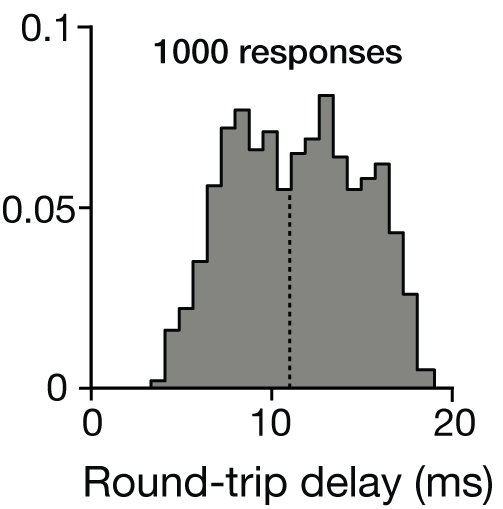
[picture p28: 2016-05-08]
doc/figures/latencies/usb.png

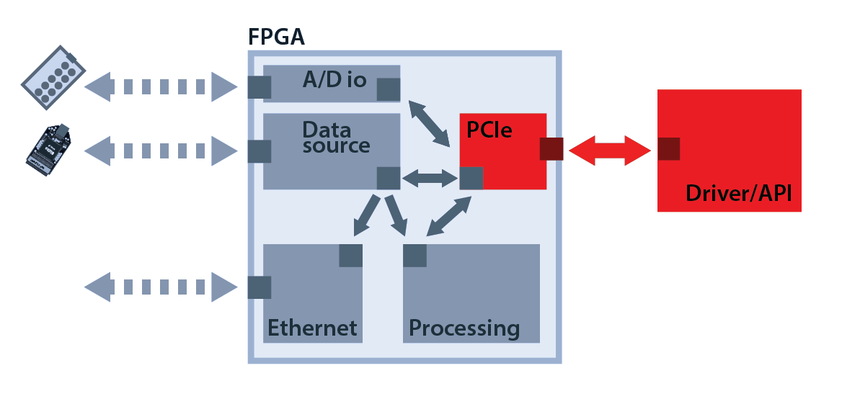
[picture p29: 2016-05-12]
doc/figures/fpga_all_DMA.png

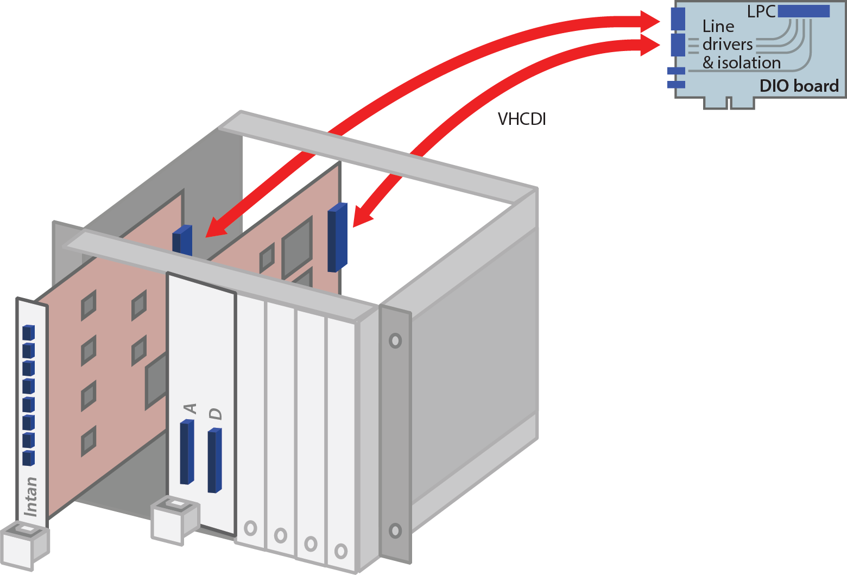
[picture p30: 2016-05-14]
doc/figures/eurocard_sketch.png

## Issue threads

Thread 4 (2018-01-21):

### ISSUE TITLE
"Striding" channels during DMA for better memory locality and easier coding

### ISSUE THREAD

**Issue by shlevy** [open-ephys/next-gen-system#4]
Some applications may want to work with blocks of several samples as a unit of input, not just a single sample. It would be nice if the driver could be configured so that, instead of putting the values for all channels for a single sample into a single contiguous region, the values were written with gaps the size of the sample block and the initial offset increased until the full block is written, so that the application can then just read a contiguous region of memory as a single channel, rather than having to jump from one sample to the next.

More concretely, call the value of the nth channel at the mth time offset Vn,m. Then a naive implementation of DMAing a 4-channel input to a circular buffer 3 samples wide might have after 3 time steps:

[ V1,1 | V2,1 | V3,1 | V4,1 | V1,2 | V2,2 | V3,2 | V4,2 | V1,3 | V2,3 | V3,3 | V4,3 ]

And then after another one

[ V1,4 | V2,4 | V3,4 | V4,4 | V1,2 | V2,2 | V3,2 | V4,2 | V1,3 | V2,3 | V3,3 | V4,3 ]

Then the application, if it wants to read say three consecutive samples from a single channel, will always have to skip at least three values, which will complicated the code (code for handling a single channel needs to know how many total channels there are) and hurt memory locality.

On the other hand, a striding implementation might have after 3 steps:

[ V1,1 | V1,2 | V1,3 | V2,1 | V2,2 | V2,3 | V3,1 | V3,2 | V3,3 | V4,1 | V4,2 | V4,3 ]

And then after another one

[ V1,4 | V1,2 | V1,3 | V2,4 | V2,2 | V2,3 | V3,4 | V3,2 | V3,3 | V4,4 | V4,2 | V4,3 ]

and single-channel processing only needs to care about a single channel, stays within a single contiguous region, and if it ensures it only processes at multiples of the block size then it doesn't need to do any jumping around at all.

**Comment by jonnew** [comment]
Thanks for this, Shea. As we discussed, this is especially important for when using multiple processors to handle data after it is collected since the division of labor between processors naturally falls into groups of channels.

The current user-land [API specification](https://github.com/open-ephys/next-gen-system/tree/master/API) specifies nothing about the nature of data being produces by a device except its location and block size:

``` c
int oiReadStream(oiContext c, int port, int stream, int nbytes, void *data)
```

The reason for this is that we did not want to make predictions about the various types of data that would be collected with the system. For instance, if people collecting calcium imaging data were to use the system, then the alignment specialization you propose might be a performance hindrance rather than a help.

You mention that alignment should be a configurable option in the driver. How would one go about that? Do you think we can make this configurable from the user-level application at runtime?

**Comment by shlevy** [comment]
I started answering your question and realized that, from a very generic viewpoint, there are a number of possible parameters relating to how memory is filled by the driver spatially that you could be asking about:
1. The type of an individual value. Maybe for some systems this is a double (representing voltage, say?) and others it's a boolean, for example. Technically could change per value source
2. The number of value sources. In the electrophysiology case this is the number of channels. I've been assuming that all sources are sampled at the same time, but technically they could be processed independently
3.  The number of samples that can be written without overwrite. In the simplest case, the system just overwrites the same memory region each sample, but in the general case a circular buffer seems to make sense here
4. Whether, in the multiple samples-without-overwrite case, the values are written sequentially in time per channel or sequentially in channels per time (this is the striding question)

1 and 2 are fixed in hardware, but it seems like both 3 and 4 are application specific and should be configurable by user-level code. My application might want to process each sample independently, so I set the overwrite number to 1 and don't care about striding. You want to process blocks of samples and have each source be handled contiguously, so you set the overwrite number to (some multiple of) the size of your processing blocks and set up striding.

**Comment by aacuevas** [comment]
One thing to have in mind is that we aren't specifically targeting multichannel systems with our API, but just raw data streams. The data could be raw channels from an ephys system, frames from a video capture device, multimedia streams or any kind of already processed digital data blocks from a device that does its own data processing. 
The way the data is sent is, thus, not the responsibility of the driver but of the device/firmware sending the data.

Striding options, if I'm understanding this correctly, would mean the driver mangling the data received by the device. As far as I know, that doesn't work well with the way DMA transfer data (in blocks which in most cases won't match the "block size" of the actual data). Mangling data here is also a bad idea, since we could have multiple readers accessing the same low-level buffer, each with their own requirements.
Where this could be done, albeit with a performance loss (a flat `memcpy`is always faster than juggling with the data) is in the `oiReadStream`function, which copies data from the low-level buffer into a local buffer.

Enter the `oiSetStreamAttributes` function. This hardly defined function can alter the way the writeStream and readStream calls work. In our idea for the default mode, the DMA just copies data into the memory buffer as soon as it is available, then the user calls oiReadStream with a number of desired bytes and the call returns reading as many bytes as it could up to the specified number (returning the actual number of read bytes, without blocking). Changing the attributes we could make, for example, the read call to block until the desired number of bytes is available (or a timeout triggers). So, for example, we could add some striding options here and let the read function do the transposing work for you, instead of requiring an extra memory operation in the user code. In fact, I quite like this approach since we can make it quite generic and it could improve performance in some cases.

**Comment by shlevy** [comment]
Closing this to clear up my open issues list, please open a new one if interested in pursuing this.

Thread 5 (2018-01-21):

### ISSUE TITLE
Facilities for zero-copy sharing of DMA region between multiple processes

### ISSUE THREAD

**Issue by shlevy** [open-ephys/next-gen-system#5]
The API should expose a way to have multiple processes share the DMA region without requiring any actual copying. Under the hood this could be implemented by just passing around file descriptors (either through inheritance or unix sockets) and having each process map the file descriptor into its own memory space. Whether the API exposes the file descriptor detail is optional, but IMO exposing it doesn't lose much and gives the user flexibility on exactly how the descriptor is shared between processes.

**Comment by glopesdev** [comment]
This is an interesting requirement, and could be nice to have, but we should be careful to avoid exposing OS-specific APIs to the top level (e.g. unix sockets), which would make cross-platform support harder.

However, another question is how would this be different from just sharing the pointer to the open device instance between threads? There's nothing stopping you from reading data from the same device from multiple threads, although we should think about the side effects of doing so.

**Comment by shlevy** [comment]
I'm specifically thinking of the multi-process case, where each thread of control has a separate memory space. Unless you mean "pointer" as something more generic than a memory pointer?

**Comment by shlevy** [comment]
As for cross-platform: It might be nice to eventually have a cross-platform API for sharing the mapping between processes and also platform specific ones if users want to do more complicated things (e.g. `std::thread` in the C++ stdlib has a `native_handle` function). But of course the platform specific one can come later if it's needed.

**Comment by aacuevas** [comment]
We already discussed this when designing the current API. In `int oiOpenPort(oiContext c, int port, int flags=OI_DEFAULT_FLAG)` one of the purposes of the flag is to define read/write permissions. While the specifics are still not defined, our idea was that the driver would allow only one writer, or master thread, with the ability to issue control commands and as many reader clients as needed that can just read from the streams using the `int oiReadStream(oiContext c, int port, int stream, int nbytes, void *data)` function.

We haven't discussed still the details of the concrete implementation, right now we are defining how the API should behave. However we do this, if any platform-specific element is needed it will be hidden under our API, so for the client point of view the system should be completely cross-platform.

**Comment by shlevy** [comment]
Seems like this is already covered then, cool

**Comment by aacuevas** [comment]
It's mostly covered. The oiReadStream behaves like the OS read function: it does copy the data in the underlying stream into a local buffer. Calls from different threads access the same buffer without needing additional memory operations but they do copy the data into their local memory space (the same as if you used a POSIX read in different threads with a shared file descriptor, in fact our api is heavily influenced by POSIX).

If what you mean here is a real memory map to the low-level buffer... It could be done, but since the underlying buffer is a circular buffer that it's continuously being filled with data by the DMA engine of the PCIe interface, it would be quite challenging to maintain synchronization for the client, since all the extra facilities the readStream function presents (buffer tracking, overflow error notifications, etc...) would not be present.

**Comment by shlevy** [comment]
Closing this to clear up my open issues list, please open a new one if interested in pursuing this.

**Comment by jonnew** [comment]
Reopening to keep immediately visible.

**Comment by jonnew** [comment]
Closing because I did not fully understand @shlevy's motivation for closing. I will copy this somewhere I can refer to it.

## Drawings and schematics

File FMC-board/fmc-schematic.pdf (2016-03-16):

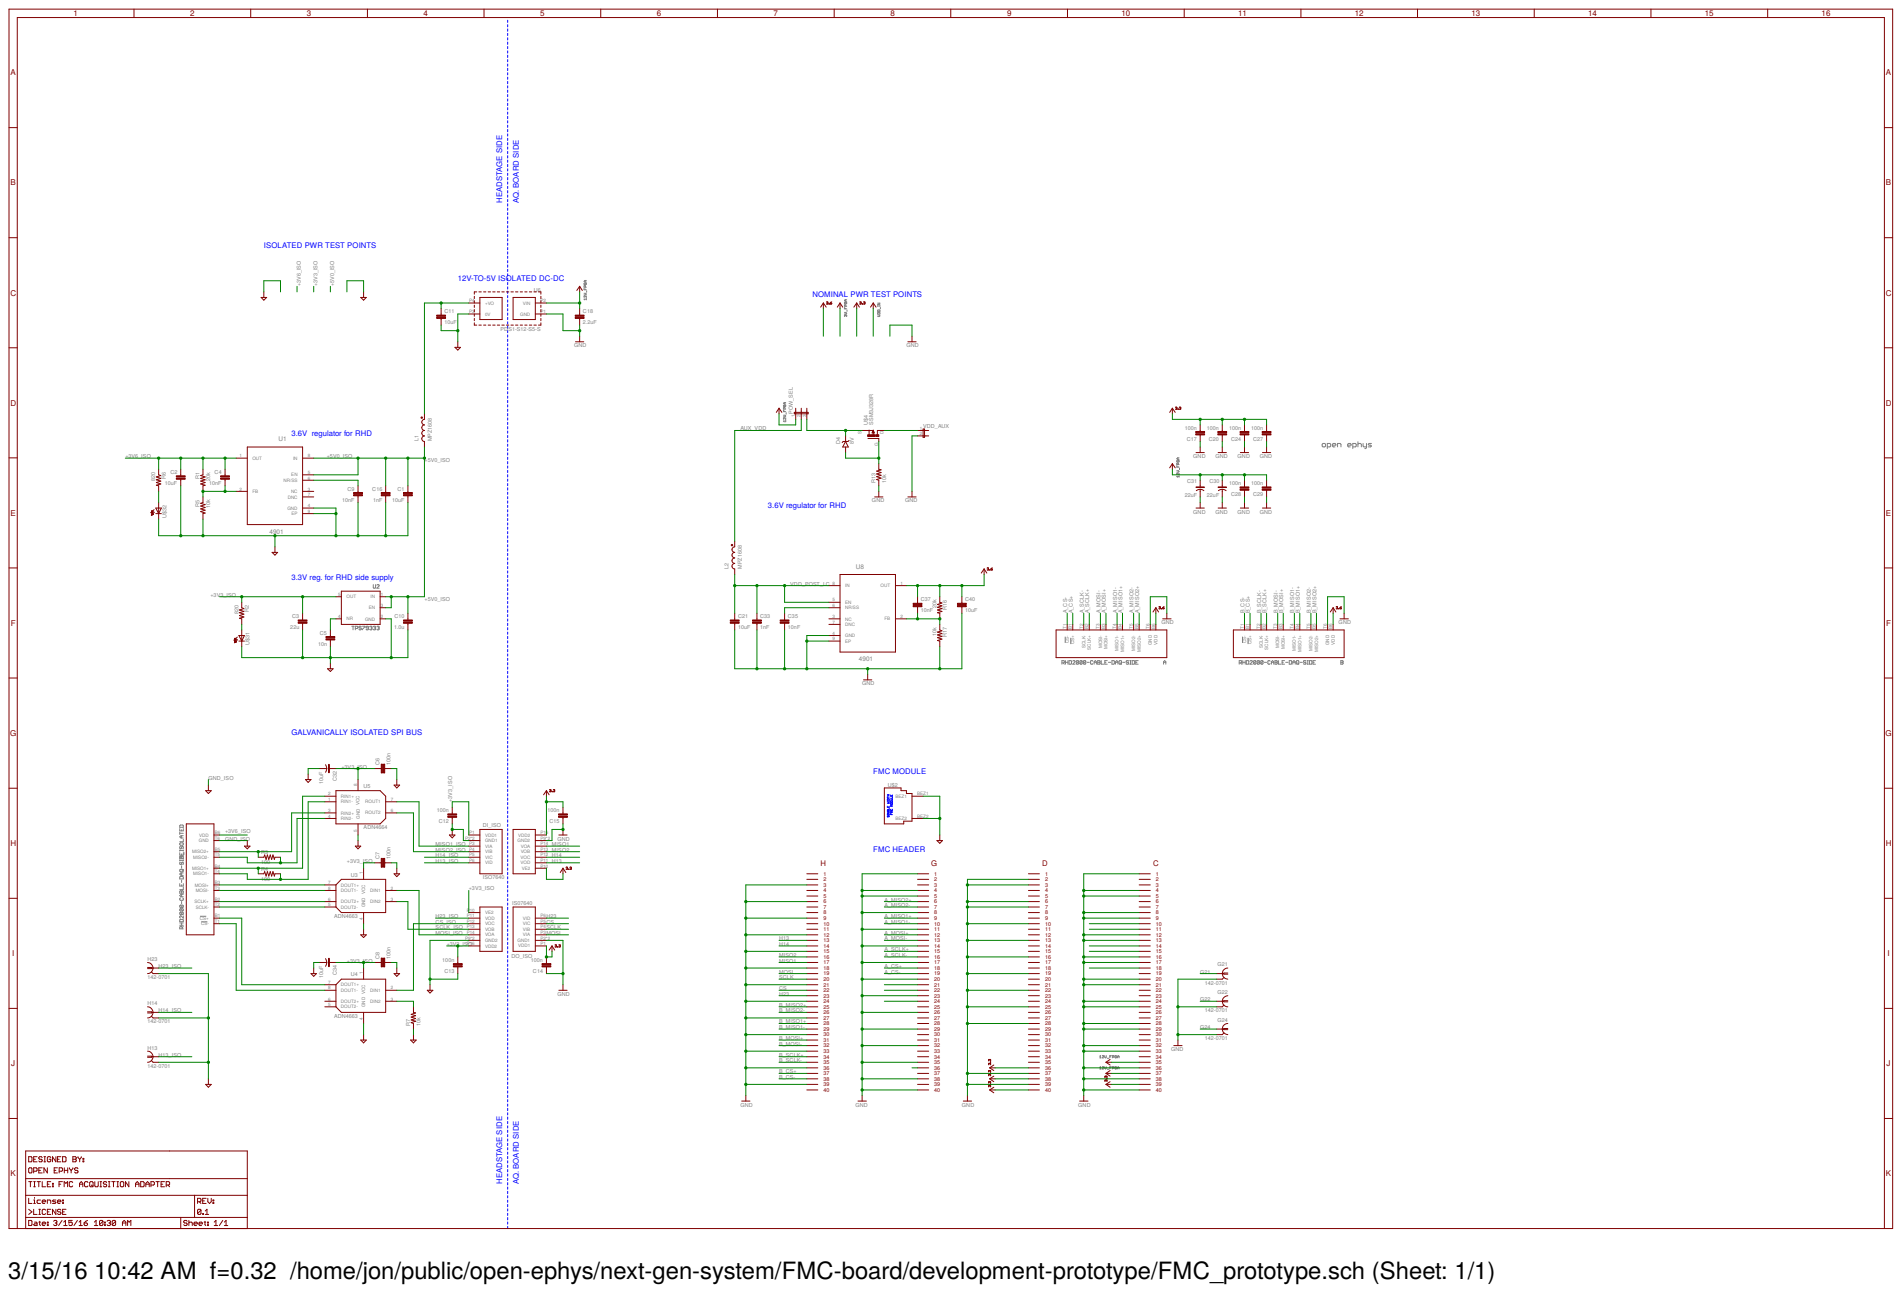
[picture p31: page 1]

12V-TO-5V ISOLATED DC-DC

3.3V reg. for RHD side supply

GALVANICALLY ISOLATED SPI BUS

3/15/16 10:42 AM f=0.32 /home/jon/public/open-ephys/next-gen-system/FMC-board/development-prototype/FMC_prototype.sch (Sheet: 1/1)

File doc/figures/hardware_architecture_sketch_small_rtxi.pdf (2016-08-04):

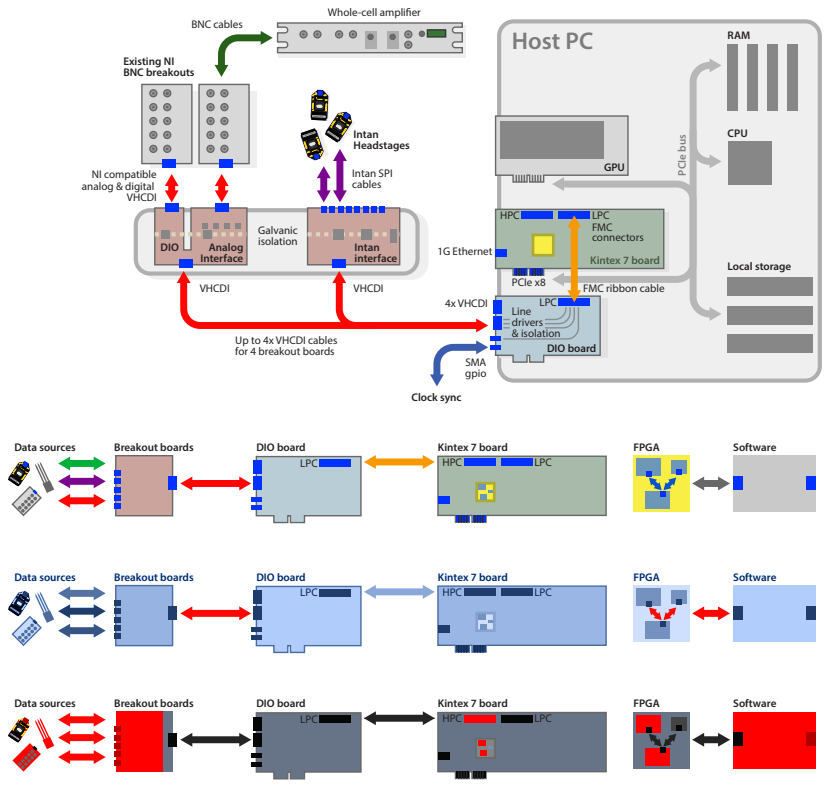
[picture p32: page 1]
RHD2132; OMNETICS 3478; Kintex 7 board; PCIe bus; DIO board; Intan interface; DIO; Analog; GPU; RAM; CPU; Local storage; Intan SPI cables; Breakout boards; Intan Headstages; Host PC; LPC; Line drivers & isolation; 1G Ethernet; SMA gpio; Clock sync; 4x VHCDI; VHCDI; NI compatible analog & digital VHCDI; BNC cables; Existing NI BNC breakouts; Galvanic isolation; PCIe x8; FMC connectors; FPGA; Software; HPC; Data sources

Whole-cell amplier

intan TECHN OLOGIES, LLC

HPC | LPC

Interface

FMC ribbon cable

Up to 4x VHCDI cables
for 4 breakout boards

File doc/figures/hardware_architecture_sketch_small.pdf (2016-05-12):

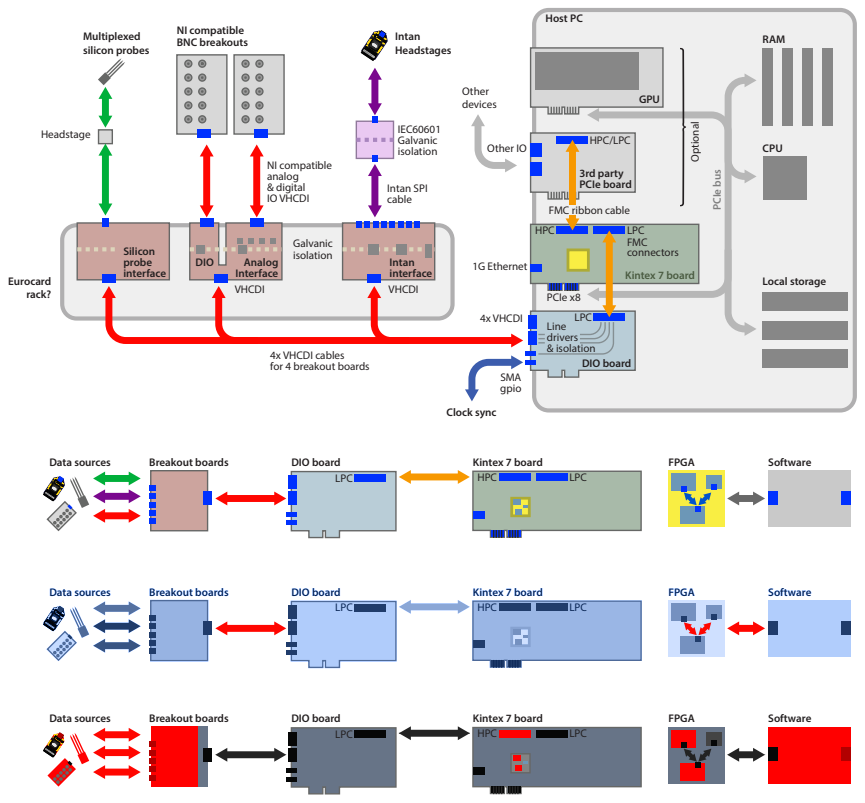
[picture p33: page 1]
OMNETICS 3478; Kintex 7 board; 3rd party PCIe board; PCIe bus; DIO board; Intan interface; Silicon probe interface; DIO; Analog; GPU; RAM; CPU; Local storage; Other IO; Other devices; Intan SPI cable; Breakout boards; Intan Headstages; Multiplexed silicon probes; Optional; Host PC; Eurocard rack?; LPC; Line drivers & isolation; 1G Ethernet; SMA gpio; Clock sync; 4x VHCDI; VHCDI; NI compatible analog & digital IO VHCDI; NI compatible BNC breakouts; Galvanic isolation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

FMC ribbon cable

HPC | LPC

Interface

4x VHCDI cables
for 4 breakout boards

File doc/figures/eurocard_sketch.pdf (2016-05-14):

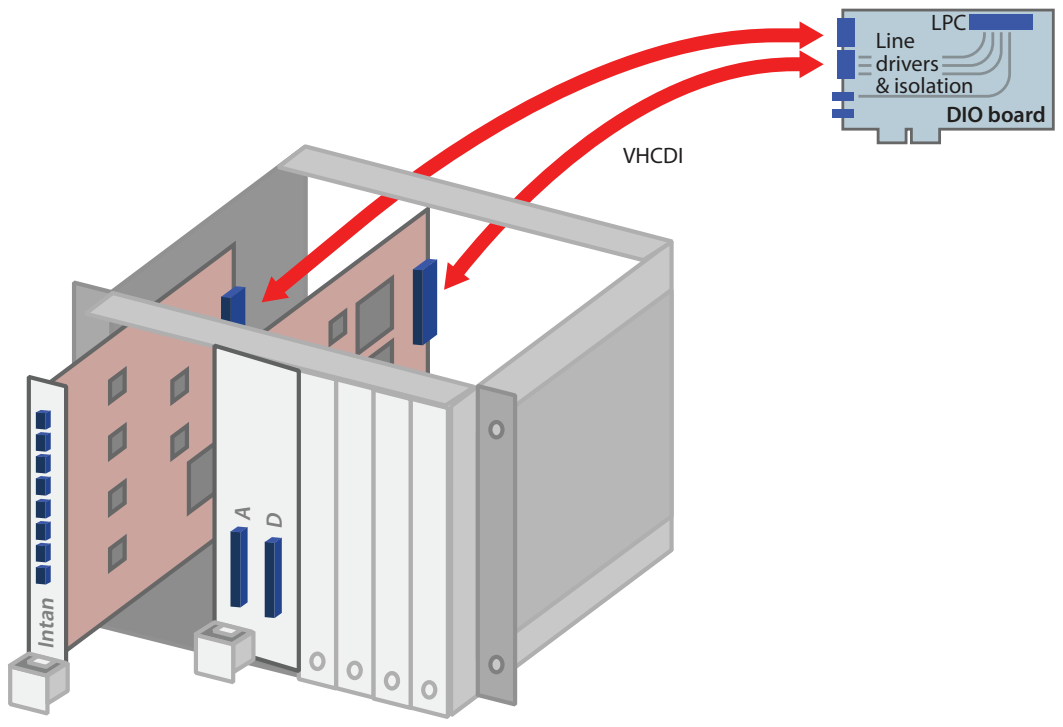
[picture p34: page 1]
DIO board; LPC; Line drivers & isolation; VHCDI; Intan

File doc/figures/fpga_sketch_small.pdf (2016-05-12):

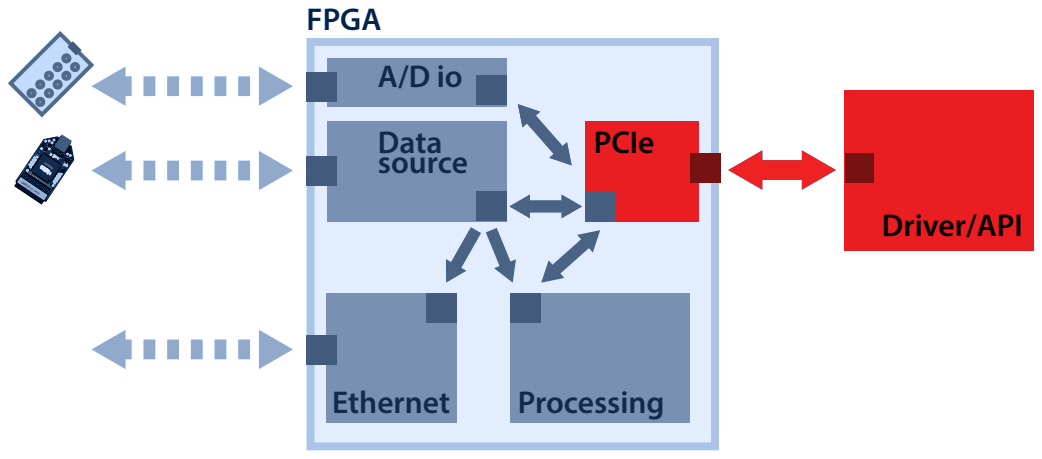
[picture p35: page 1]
Driver/API; FPGA; PCIe; Data; source OMNETICS 3478; Ethernet; Processing

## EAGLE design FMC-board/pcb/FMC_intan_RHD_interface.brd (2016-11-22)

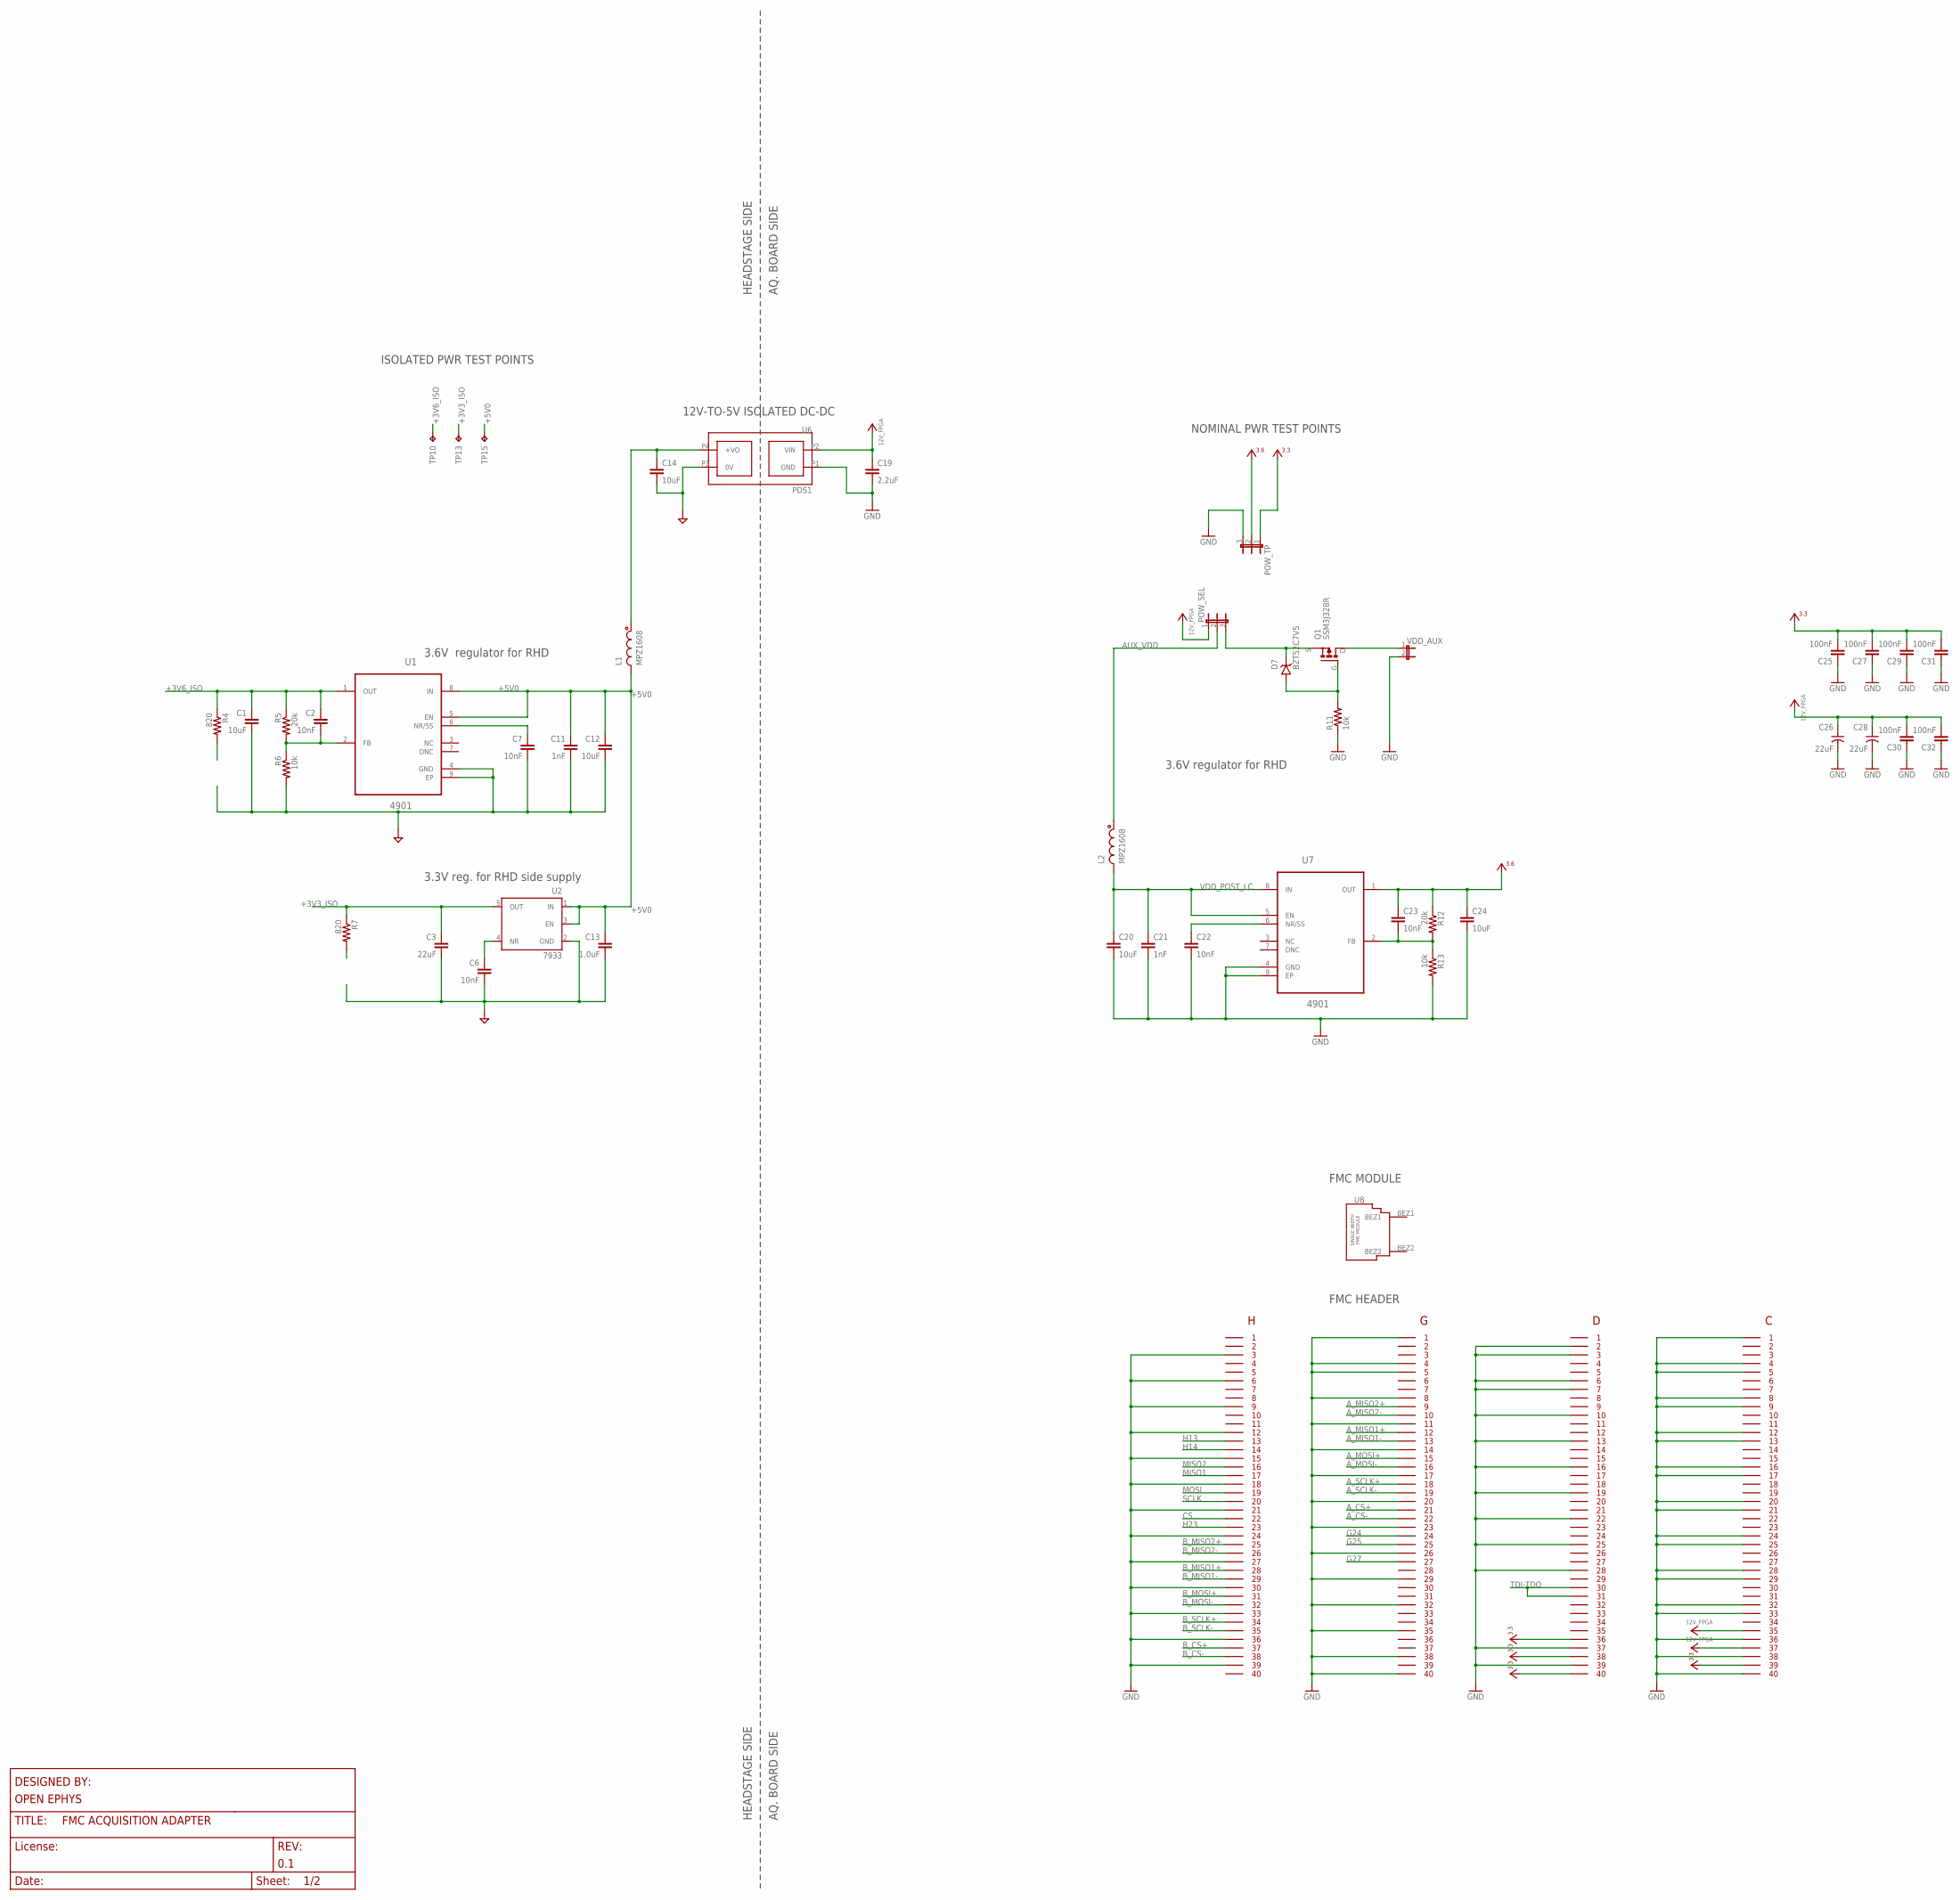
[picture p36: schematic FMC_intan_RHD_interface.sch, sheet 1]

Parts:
C1, C12, C14, C20, C24: 10uF; 1206
C2, C6, C7, C22, C23: 10nF; 0603
C3: 22uF; 1206
C11, C21: 1nF; 0603
C13: 1.0uF; 0805
C19: 2.2uF; 1206
C25, C27, C29, C30, C31, C32: 100nF; 0603
C26, C28: 22uF; 1210-POL
D7: BZT52C7V5; SOD123
FMC: FMC_LPC_160_PIN; FMC_LPC_MALE_WITH_SP601_BSILK
L1, L2: MPZ1608; 0603
POW_SEL: JP3E; JP3
POW_TP: JP3E; JP3
Q1: SSM3J328R; SOT23-GSD
R4, R7: 820; 0603
R5, R12: 20k; 0603
R6, R11, R13: 10k; 0603
TP10: +3V6; TP06R
TP13: +3V3; TP06R
TP15: +5V0; TP06R
U1, U7: 4901; SOP65P490X110-9N
U2: 7933; SOT-23-5
U6: PDS1
U8: FMC_SINGLE_WIDTH_MODULE
VDD_AUX: JP2E_THRU-HOLE; JP2

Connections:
12V_FPGA: C19.1, C26.+, C28.+, C30.2, C32.2, FMC.P$155, FMC.P$157, POW_SEL.1, U6.P2 (VIN)
+3V3: C25.2, C27.2, C29.2, C31.2, FMC.P$116, FMC.P$118, FMC.P$120, FMC.P$159, POW_TP.1; also elsewhere on the board
+3V3_ISO: C3.1, R7.1, TP13.TP, U2.5 (OUT); also elsewhere on the board
+3V6: C23.1, C24.1, POW_TP.2, R12.1, U7.1 (OUT)
+3V6_ISO: C1.1, C2.1, R4.1, R5.1, TP10.TP, U1.1 (OUT); also elsewhere on the board
+5V0: C11.1, C12.1, C13.1, L1.2, TP15.TP, U1.5 (EN), U1.8 (IN), U2.1 (IN), U2.3 (EN)
+5V0_ISO-PRE: C14.1, L1.1, U6.P4 (+VO)
AGND1: C23.2, R12.2, R13.1, U7.2 (FB)
AGND2: C2.2, R5.2, R6.1, U1.2 (FB)
AUX_VDD: L2.1, POW_SEL.2
A_CS+: FMC.P$61
A_CS-: FMC.P$62
A_MISO1+: FMC.P$52
A_MISO1-: FMC.P$53
A_MISO2+: FMC.P$49
A_MISO2-: FMC.P$50
A_MOSI+: FMC.P$55
A_MOSI-: FMC.P$56
A_SCLK+: FMC.P$58
A_SCLK-: FMC.P$59
B_CS+: FMC.P$37
B_CS-: FMC.P$38
B_MISO1+: FMC.P$28
B_MISO1-: FMC.P$29
B_MISO2+: FMC.P$25
B_MISO2-: FMC.P$26
B_MOSI+: FMC.P$31
B_MOSI-: FMC.P$32
B_SCLK+: FMC.P$34
B_SCLK-: FMC.P$35
CS: FMC.P$22; also elsewhere on the board
G24: FMC.P$64
G25: FMC.P$65
G27: FMC.P$67
GND: C19.2, C20.2, C21.2, C22.2, C24.2, C25.1, C26.-, C27.1, C28.-, C29.1, C30.1, C31.1, C32.1, FMC.GNDA (GND), FMC.GNDB (GND), FMC.P$3, FMC.P$6, FMC.P$9, FMC.P$12, FMC.P$15, FMC.P$18, FMC.P$21, FMC.P$24, FMC.P$27, FMC.P$30, FMC.P$33, FMC.P$36, FMC.P$39, FMC.P$41, FMC.P$44, FMC.P$45, FMC.P$48, FMC.P$51, FMC.P$54, FMC.P$57, FMC.P$60, FMC.P$63, FMC.P$66, FMC.P$69, FMC.P$72, FMC.P$75, FMC.P$78, FMC.P$80, FMC.P$82, FMC.P$83, FMC.P$86, FMC.P$87, FMC.P$90, FMC.P$93, FMC.P$96, FMC.P$99, FMC.P$102, FMC.P$105, FMC.P$108, FMC.P$117, FMC.P$119, FMC.P$121, FMC.P$124, FMC.P$125, FMC.P$128, FMC.P$129, FMC.P$132, FMC.P$133, FMC.P$136, FMC.P$137, FMC.P$140, FMC.P$141, FMC.P$144, FMC.P$145, FMC.P$148, FMC.P$149, FMC.P$152, FMC.P$153, FMC.P$156, FMC.P$158, FMC.P$160, POW_TP.3, R11.1, R13.2, U6.P1 (GND), U7.4 (GND), U7.9 (EP), VDD_AUX.2; also elsewhere on the board
GND_ISO: C1.2, C3.2, C6.2, C7.2, C11.2, C12.2, C13.2, C14.2, R6.2, U1.4 (GND), U1.9 (EP), U2.2 (GND), U6.P3 (0V); also elsewhere on the board
H13: FMC.P$13; also elsewhere on the board
H14: FMC.P$14; also elsewhere on the board
H23: FMC.P$23; also elsewhere on the board
MISO1: FMC.P$17; also elsewhere on the board
MISO2: FMC.P$16; also elsewhere on the board
MOSI: FMC.P$19; also elsewhere on the board
unnamed: C22.1, U7.6 (NR/SS)
unnamed: D7.C, POW_SEL.3, Q1.S
unnamed: C7.1, U1.6 (NR/SS)
unnamed: D7.A, Q1.G, R11.2
unnamed: Q1.D, VDD_AUX.1
unnamed: C6.1, U2.4 (NR)
SCLK: FMC.P$20; also elsewhere on the board
TDI-TDO: FMC.P$110, FMC.P$111
VDD_POST_LC: C20.1, C21.1, L2.2, U7.5 (EN), U7.8 (IN)

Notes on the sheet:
HEADSTAGE SIDE
AQ. BOARD SIDE
3.3V reg. for RHD side supply
3.6V regulator for RHD
12V-TO-5V ISOLATED DC-DC
ISOLATED PWR TEST POINTS
NOMINAL PWR TEST POINTS
3.6V regulator for RHD
FMC HEADER
FMC MODULE

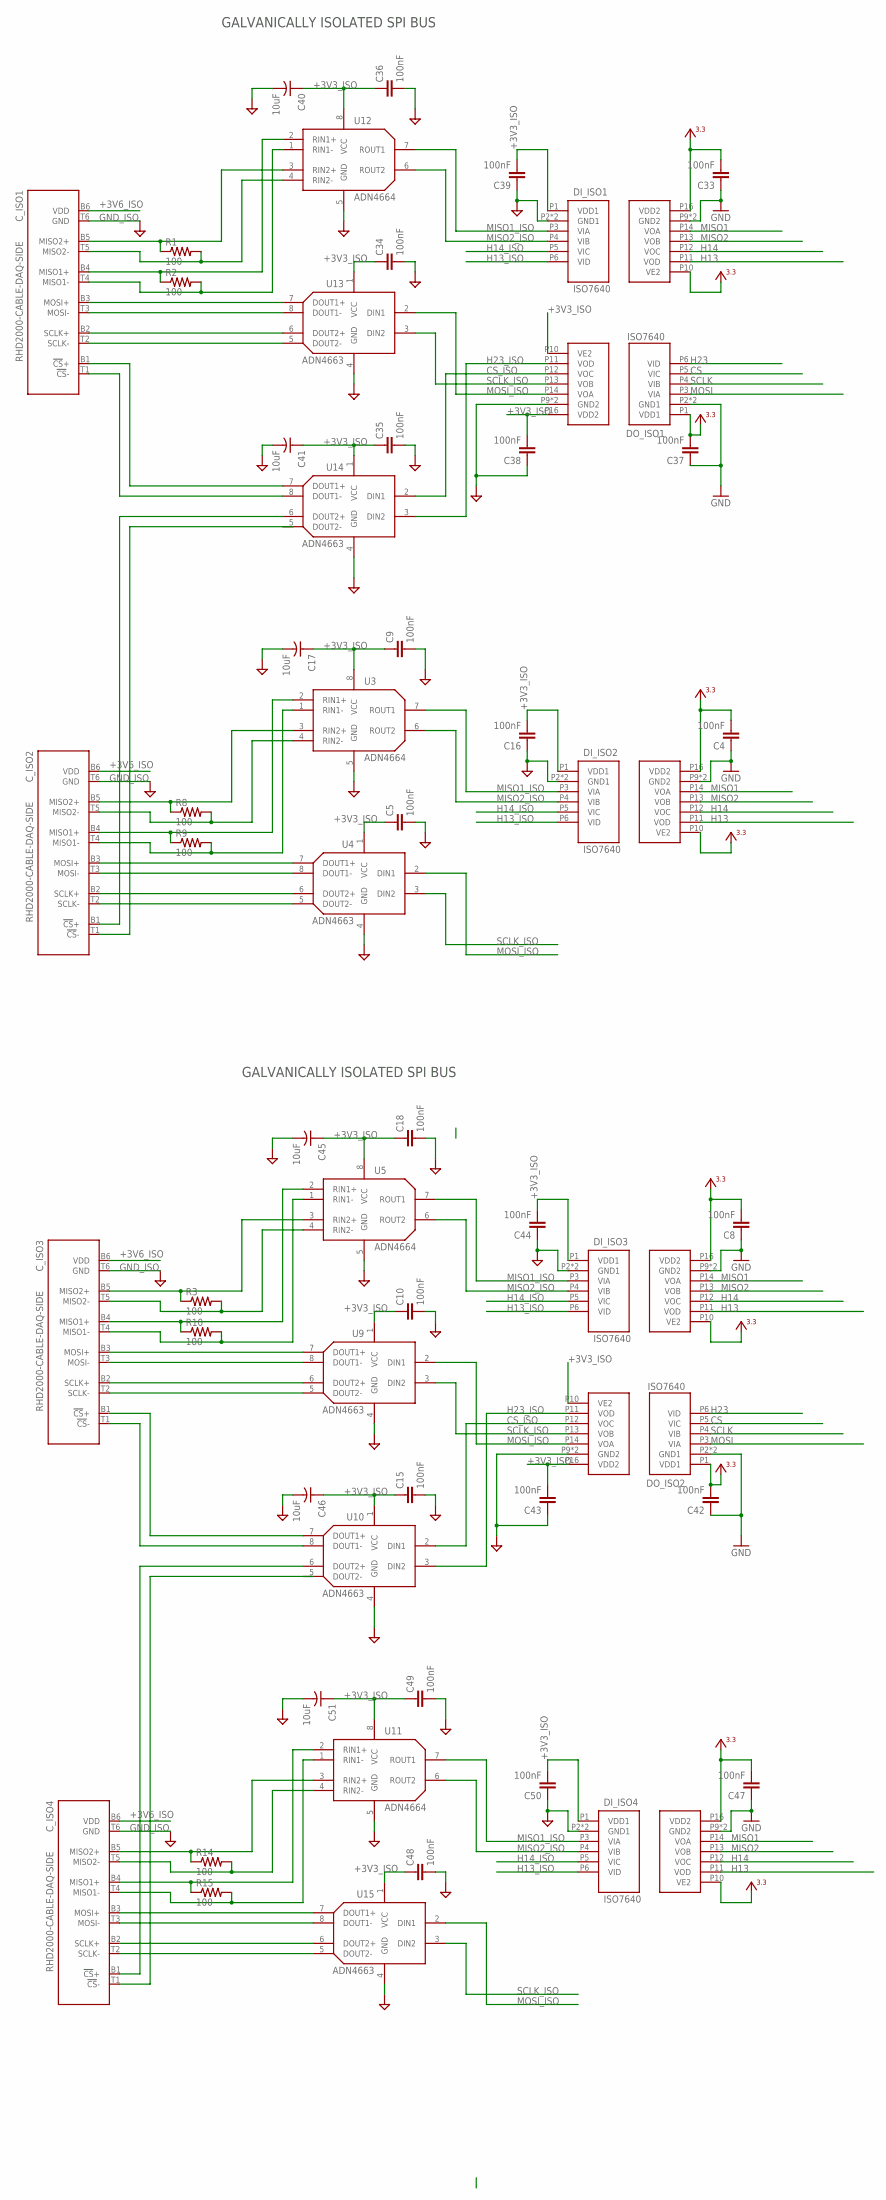
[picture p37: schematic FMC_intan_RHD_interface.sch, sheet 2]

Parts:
C4, C5, C8, C9, C10, C15, C16, C18, C33, C34, C35, C36, C37, C38, C39, C42, C43, C44, C47, C48, C49, C50: 100nF; 0603
C17, C40, C41, C45, C46, C51: 10uF; 1206-POL
C_ISO1, C_ISO2, C_ISO3, C_ISO4: RHD2000-CABLE-DAQ-SIDE; OMNETICS_PZN-12-AA
DI_ISO1, DI_ISO2, DI_ISO3, DI_ISO4: ISO7640; SOIC_WIDE_16
DO_ISO1, DO_ISO2: ISO7640; SOIC_WIDE_16
R1, R2, R3, R8, R9, R10, R14, R15: 100; 0603
U3, U5, U11, U12: ADN4664; SOIC127P500X400-8N
U4, U9, U10, U13, U14, U15: ADN4663; SOIC127P500X400-8N

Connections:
+3V3: C4.2, C8.2, C33.2, C37.2, C42.2, C47.2, DI_ISO1.P10 (VE2), DI_ISO1.P16 (VDD2), DI_ISO2.P10 (VE2), DI_ISO2.P16 (VDD2), DI_ISO3.P10 (VE2), DI_ISO3.P16 (VDD2), DI_ISO4.P10 (VE2), DI_ISO4.P16 (VDD2), DO_ISO1.P1 (VDD1), DO_ISO2.P1 (VDD1); also elsewhere on the board
+3V3_ISO: C5.1, C9.1, C10.1, C15.1, C16.2, C17.+, C18.1, C34.1, C35.1, C36.1, C38.2, C39.2, C40.+, C41.+, C43.2, C44.2, C45.+, C46.+, C48.1, C49.1, C50.2, C51.+, DI_ISO1.P1 (VDD1), DI_ISO2.P1 (VDD1), DI_ISO3.P1 (VDD1), DI_ISO4.P1 (VDD1), DO_ISO1.P10 (VE2), DO_ISO1.P16 (VDD2), DO_ISO2.P10 (VE2), DO_ISO2.P16 (VDD2), U3.8 (VCC), U4.1 (VCC), U5.8 (VCC), U9.1 (VCC), U10.1 (VCC), U11.8 (VCC), U12.8 (VCC), U13.1 (VCC), U14.1 (VCC), U15.1 (VCC); also elsewhere on the board
+3V6_ISO: C_ISO1.B6 (VDD), C_ISO2.B6 (VDD), C_ISO3.B6 (VDD), C_ISO4.B6 (VDD); also elsewhere on the board
CS: DO_ISO1.P5 (VIC), DO_ISO2.P5 (VIC); also elsewhere on the board
CS+_ISOLATED1: C_ISO1.B1 (!CS!+), U14.7 (DOUT1+)
CS+_ISOLATED2: C_ISO2.B1 (!CS!+)
CS+_ISOLATED3: C_ISO3.B1 (!CS!+), U10.7 (DOUT1+)
CS+_ISOLATED4: C_ISO4.B1 (!CS!+)
CS-_ISOLATED1: C_ISO1.T1 (!CS!-), U14.8 (DOUT1-)
CS-_ISOLATED2: C_ISO2.T1 (!CS!-)
CS-_ISOLATED3: C_ISO3.T1 (!CS!-), U10.8 (DOUT1-)
CS-_ISOLATED4: C_ISO4.T1 (!CS!-)
CS_ISO: DO_ISO1.P12 (VOC), DO_ISO2.P12 (VOC), U10.2 (DIN1), U14.2 (DIN1)
GND: C4.1, C8.1, C33.1, C37.1, C42.1, C47.1, DI_ISO1.P9 (GND2), DI_ISO1.P15 (GND2), DI_ISO2.P9 (GND2), DI_ISO2.P15 (GND2), DI_ISO3.P9 (GND2), DI_ISO3.P15 (GND2), DI_ISO4.P9 (GND2), DI_ISO4.P15 (GND2), DO_ISO1.P2 (GND1), DO_ISO1.P8 (GND1), DO_ISO2.P2 (GND1), DO_ISO2.P8 (GND1); also elsewhere on the board
GND_ISO: C5.2, C9.2, C10.2, C15.2, C16.1, C17.-, C18.2, C34.2, C35.2, C36.2, C38.1, C39.1, C40.-, C41.-, C43.1, C44.1, C45.-, C46.-, C48.2, C49.2, C50.1, C51.-, C_ISO1.T6 (GND), C_ISO2.T6 (GND), C_ISO3.T6 (GND), C_ISO4.T6 (GND), DI_ISO1.P2 (GND1), DI_ISO1.P8 (GND1), DI_ISO2.P2 (GND1), DI_ISO2.P8 (GND1), DI_ISO3.P2 (GND1), DI_ISO3.P8 (GND1), DI_ISO4.P2 (GND1), DI_ISO4.P8 (GND1), DO_ISO1.P9 (GND2), DO_ISO1.P15 (GND2), DO_ISO2.P9 (GND2), DO_ISO2.P15 (GND2), U3.5 (GND), U4.4 (GND), U5.5 (GND), U9.4 (GND), U10.4 (GND), U11.5 (GND), U12.5 (GND), U13.4 (GND), U14.4 (GND), U15.4 (GND); also elsewhere on the board
H13: DI_ISO1.P11 (VOD), DI_ISO2.P11 (VOD), DI_ISO3.P11 (VOD), DI_ISO4.P11 (VOD); also elsewhere on the board
H13_ISO: DI_ISO1.P6 (VID), DI_ISO2.P6 (VID), DI_ISO3.P6 (VID), DI_ISO4.P6 (VID)
H14: DI_ISO1.P12 (VOC), DI_ISO2.P12 (VOC), DI_ISO3.P12 (VOC), DI_ISO4.P12 (VOC); also elsewhere on the board
H14_ISO: DI_ISO1.P5 (VIC), DI_ISO2.P5 (VIC), DI_ISO3.P5 (VIC), DI_ISO4.P5 (VIC)
H23: DO_ISO1.P6 (VID), DO_ISO2.P6 (VID); also elsewhere on the board
H23_ISO: DO_ISO1.P11 (VOD), DO_ISO2.P11 (VOD), U10.3 (DIN2), U14.3 (DIN2)
MISO1: DI_ISO1.P14 (VOA), DI_ISO2.P14 (VOA), DI_ISO3.P14 (VOA), DI_ISO4.P14 (VOA); also elsewhere on the board
MISO1+_ISOLATED1: C_ISO1.B4 (MISO1+), R2.1, U12.2 (RIN1+)
MISO1+_ISOLATED2: C_ISO2.B4 (MISO1+), R9.1, U3.2 (RIN1+)
MISO1+_ISOLATED3: C_ISO3.B4 (MISO1+), R10.1, U5.2 (RIN1+)
MISO1+_ISOLATED4: C_ISO4.B4 (MISO1+), R15.1, U11.2 (RIN1+)
MISO1-_ISOLATED1: C_ISO1.T4 (MISO1-), R2.2, U12.1 (RIN1-)
MISO1-_ISOLATED2: C_ISO2.T4 (MISO1-), R9.2, U3.1 (RIN1-)
MISO1-_ISOLATED3: C_ISO3.T4 (MISO1-), R10.2, U5.1 (RIN1-)
MISO1-_ISOLATED4: C_ISO4.T4 (MISO1-), R15.2, U11.1 (RIN1-)
MISO1_ISO: DI_ISO1.P3 (VIA), DI_ISO2.P3 (VIA), DI_ISO3.P3 (VIA), DI_ISO4.P3 (VIA), U3.7 (ROUT1), U5.7 (ROUT1), U11.7 (ROUT1), U12.7 (ROUT1)
MISO2: DI_ISO1.P13 (VOB), DI_ISO2.P13 (VOB), DI_ISO3.P13 (VOB), DI_ISO4.P13 (VOB); also elsewhere on the board
MISO2+_ISOLATED1: C_ISO1.B5 (MISO2+), R1.1, U12.3 (RIN2+)
MISO2+_ISOLATED2: C_ISO2.B5 (MISO2+), R8.1, U3.3 (RIN2+)
MISO2+_ISOLATED3: C_ISO3.B5 (MISO2+), R3.1, U5.3 (RIN2+)
MISO2+_ISOLATED4: C_ISO4.B5 (MISO2+), R14.1, U11.3 (RIN2+)
MISO2-_ISOLATED1: C_ISO1.T5 (MISO2-), R1.2, U12.4 (RIN2-)
MISO2-_ISOLATED2: C_ISO2.T5 (MISO2-), R8.2, U3.4 (RIN2-)
MISO2-_ISOLATED3: C_ISO3.T5 (MISO2-), R3.2, U5.4 (RIN2-)
MISO2-_ISOLATED4: C_ISO4.T5 (MISO2-), R14.2, U11.4 (RIN2-)
MISO2_ISO: DI_ISO1.P4 (VIB), DI_ISO2.P4 (VIB), DI_ISO3.P4 (VIB), DI_ISO4.P4 (VIB), U3.6 (ROUT2), U5.6 (ROUT2), U11.6 (ROUT2), U12.6 (ROUT2)
MOSI: DO_ISO1.P3 (VIA), DO_ISO2.P3 (VIA); also elsewhere on the board
MOSI_ISO: DO_ISO1.P14 (VOA), DO_ISO2.P14 (VOA), U4.2 (DIN1), U9.2 (DIN1), U13.2 (DIN1), U15.2 (DIN1)
unnamed: C_ISO3.B3 (MOSI+), U9.7 (DOUT1+)
unnamed: C_ISO1.B3 (MOSI+), U13.7 (DOUT1+)
unnamed: C_ISO1.T3 (MOSI-), U13.8 (DOUT1-)
unnamed: C_ISO2.B3 (MOSI+), U4.7 (DOUT1+)
unnamed: C_ISO2.T3 (MOSI-), U4.8 (DOUT1-)
unnamed: C_ISO1.B2 (SCLK+), U13.6 (DOUT2+)
unnamed: C_ISO2.B2 (SCLK+), U4.6 (DOUT2+)
unnamed: C_ISO2.T2 (SCLK-), U4.5 (DOUT2-)
unnamed: C_ISO1.T2 (SCLK-), U13.5 (DOUT2-)
unnamed: C_ISO3.T3 (MOSI-), U9.8 (DOUT1-)
unnamed: C_ISO3.B2 (SCLK+), U9.6 (DOUT2+)
unnamed: C_ISO3.T2 (SCLK-), U9.5 (DOUT2-)
unnamed: C_ISO4.B3 (MOSI+), U15.7 (DOUT1+)
unnamed: C_ISO4.T3 (MOSI-), U15.8 (DOUT1-)
unnamed: C_ISO4.B2 (SCLK+), U15.6 (DOUT2+)
unnamed: C_ISO4.T2 (SCLK-), U15.5 (DOUT2-)
SCLK: DO_ISO1.P4 (VIB), DO_ISO2.P4 (VIB); also elsewhere on the board
SCLK_ISO: DO_ISO1.P13 (VOB), DO_ISO2.P13 (VOB), U4.3 (DIN2), U9.3 (DIN2), U13.3 (DIN2), U15.3 (DIN2)

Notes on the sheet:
GALVANICALLY ISOLATED SPI BUS

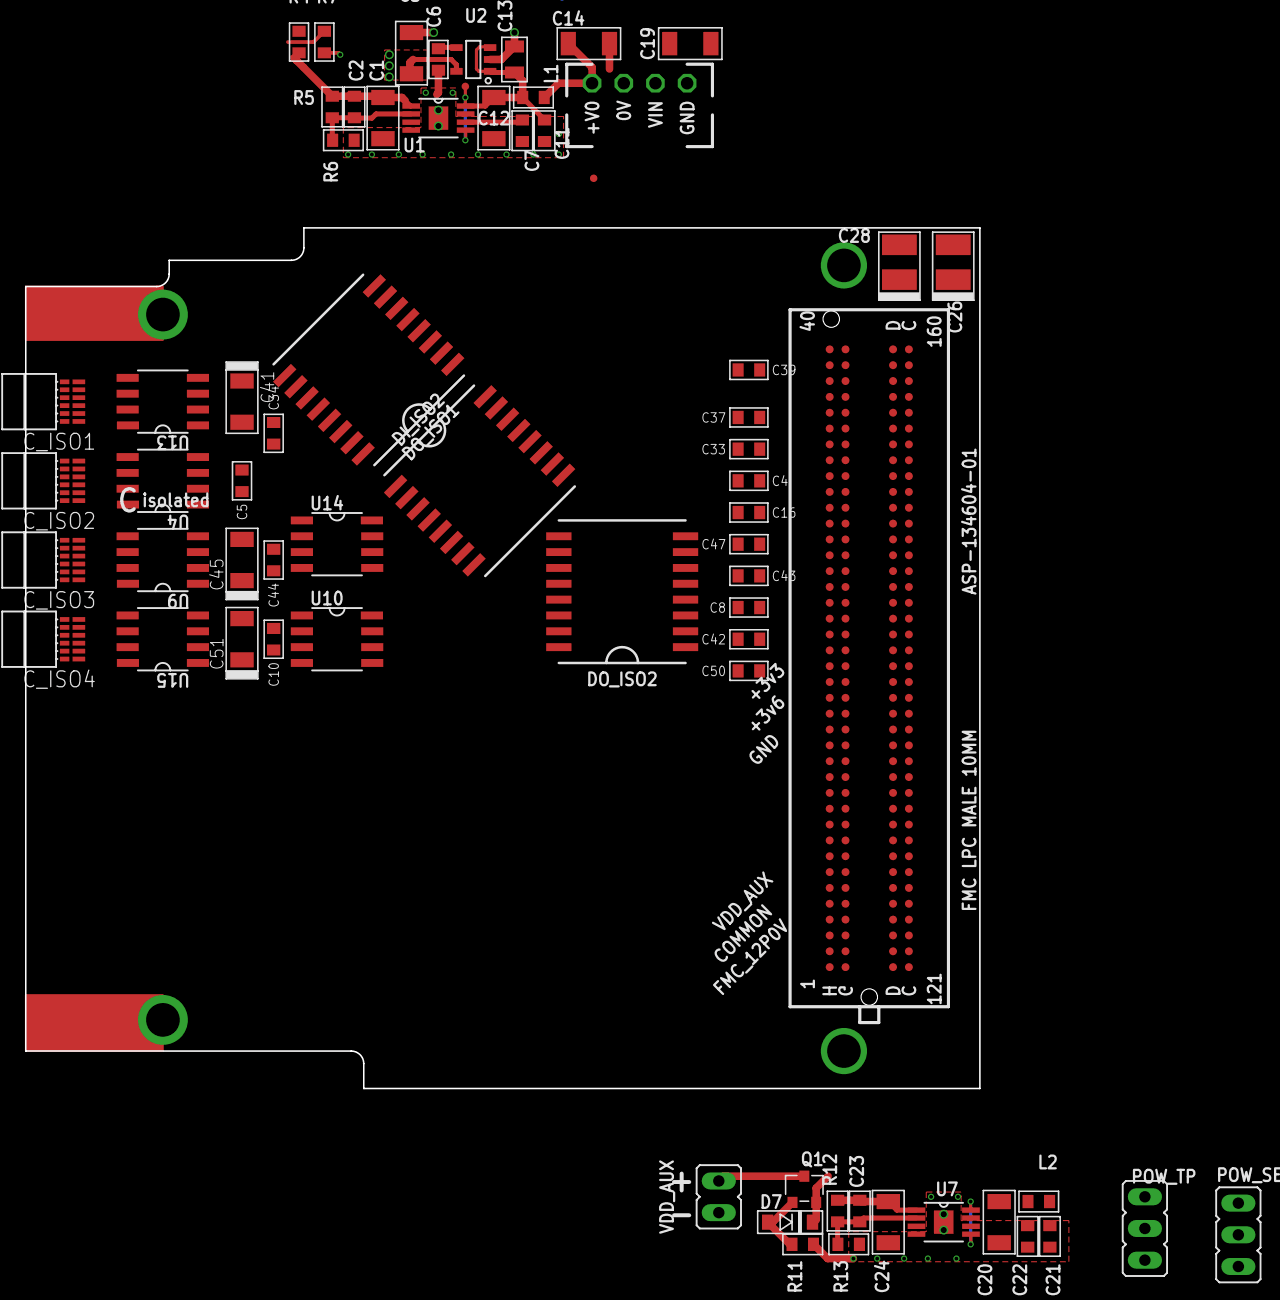
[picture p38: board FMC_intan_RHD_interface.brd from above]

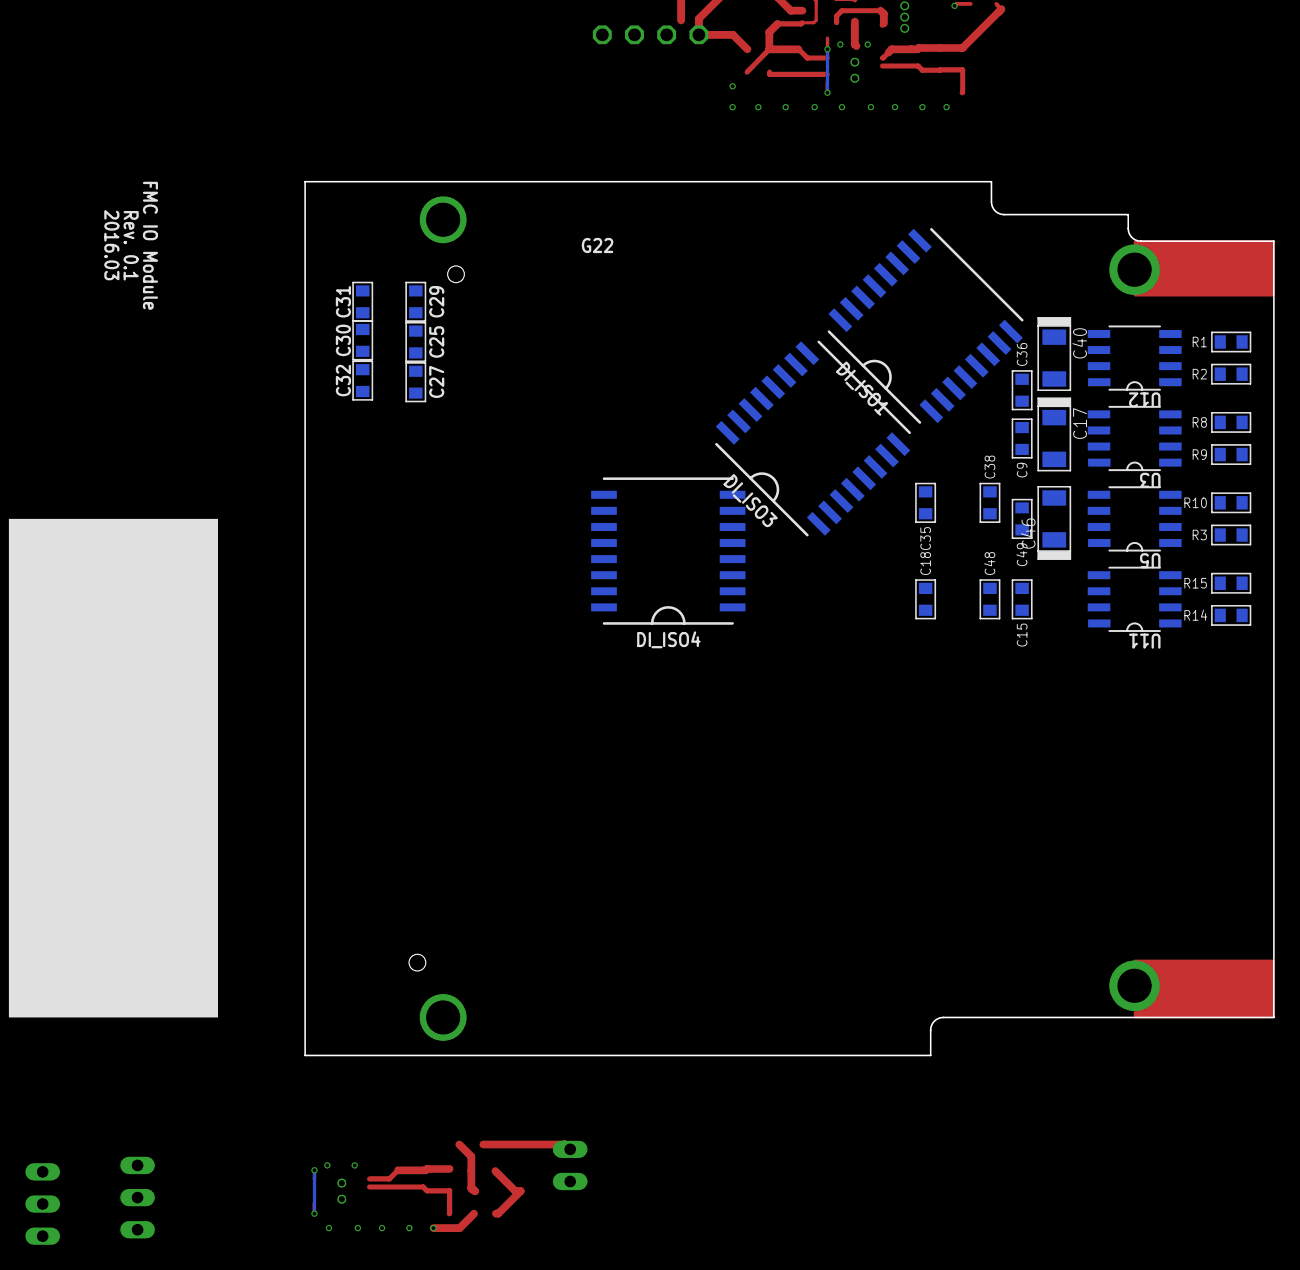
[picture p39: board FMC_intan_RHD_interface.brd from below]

Board: 4 copper layers, 76.5 x 69.0 mm, 102 parts (33 on the bottom side), 72 nets.

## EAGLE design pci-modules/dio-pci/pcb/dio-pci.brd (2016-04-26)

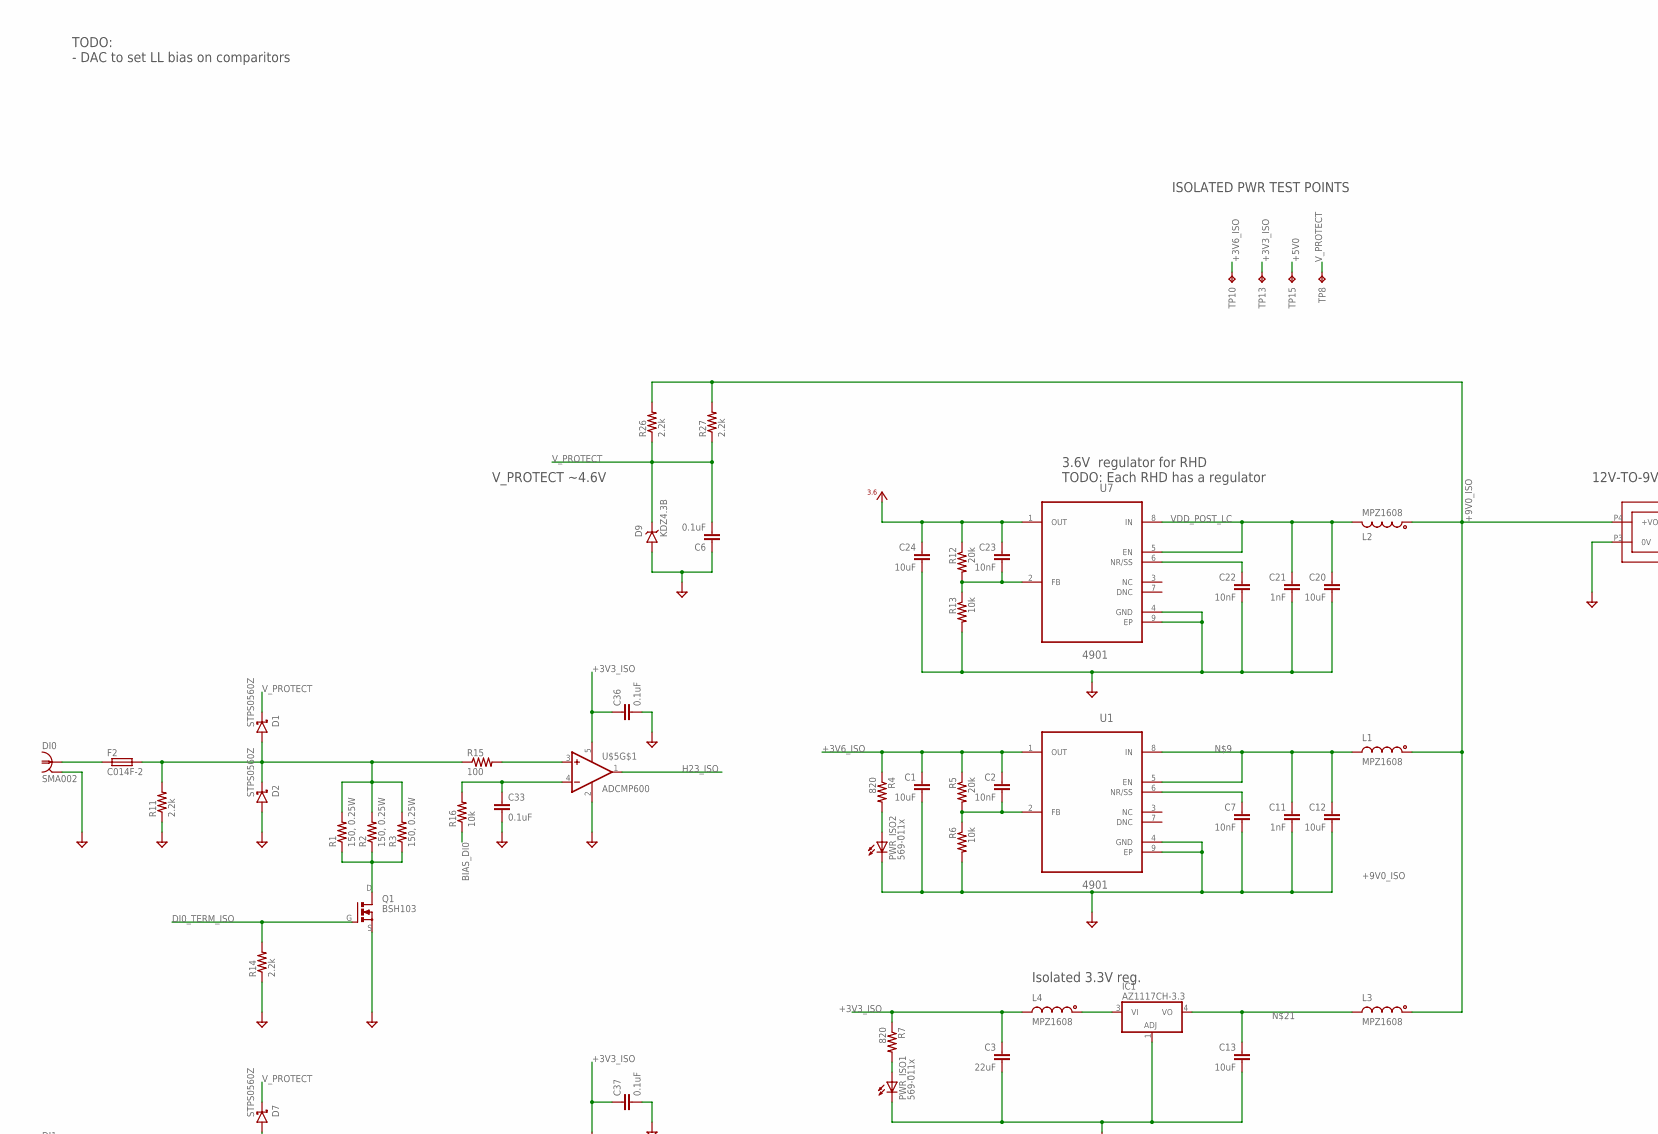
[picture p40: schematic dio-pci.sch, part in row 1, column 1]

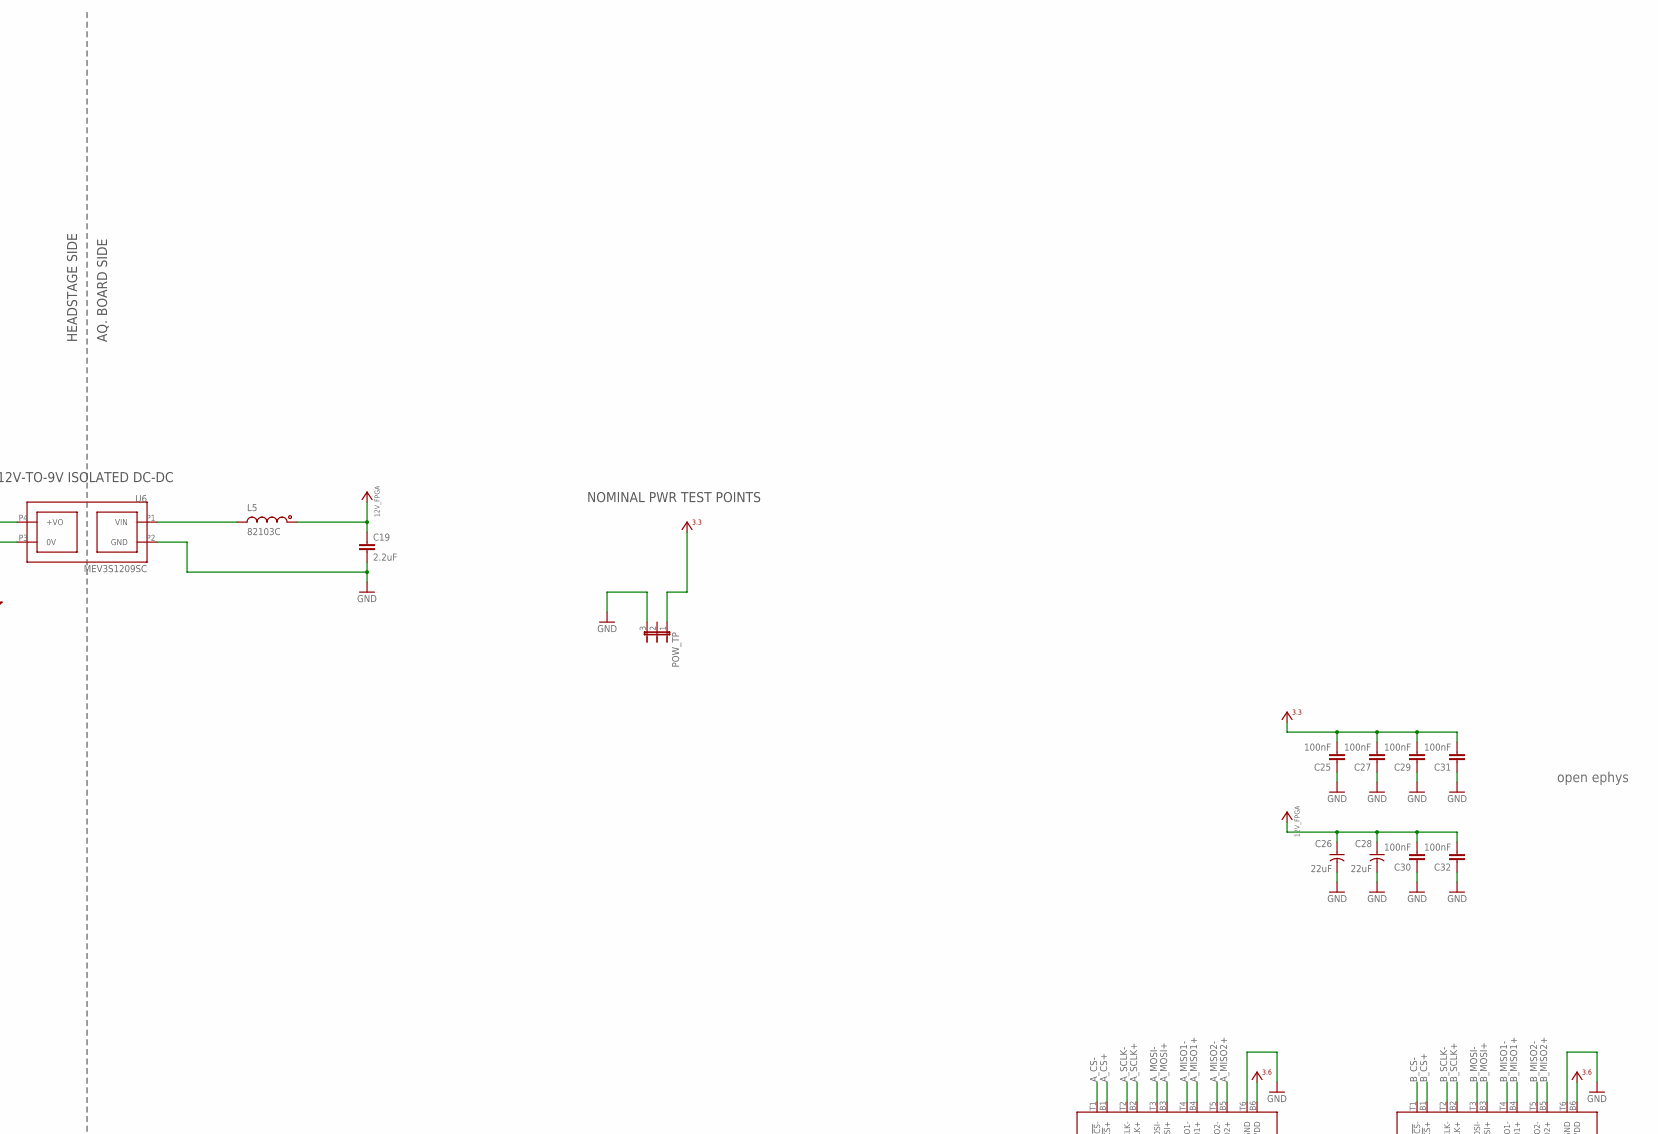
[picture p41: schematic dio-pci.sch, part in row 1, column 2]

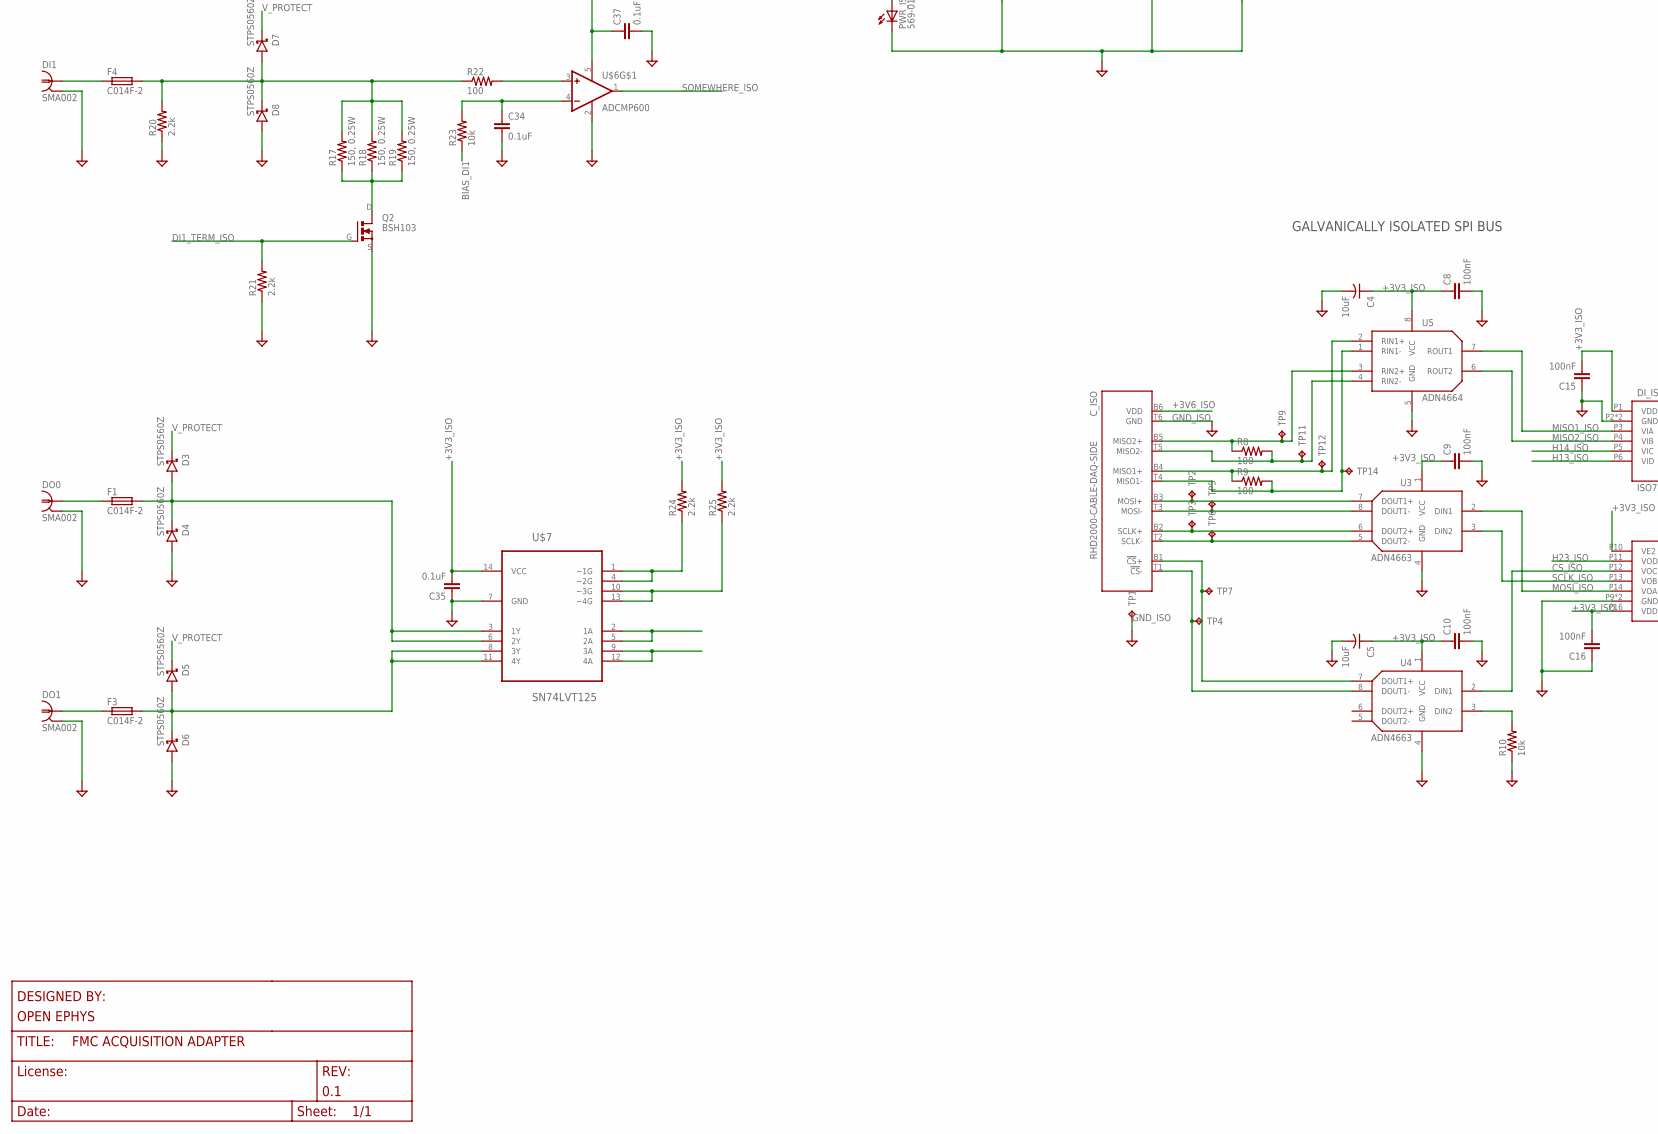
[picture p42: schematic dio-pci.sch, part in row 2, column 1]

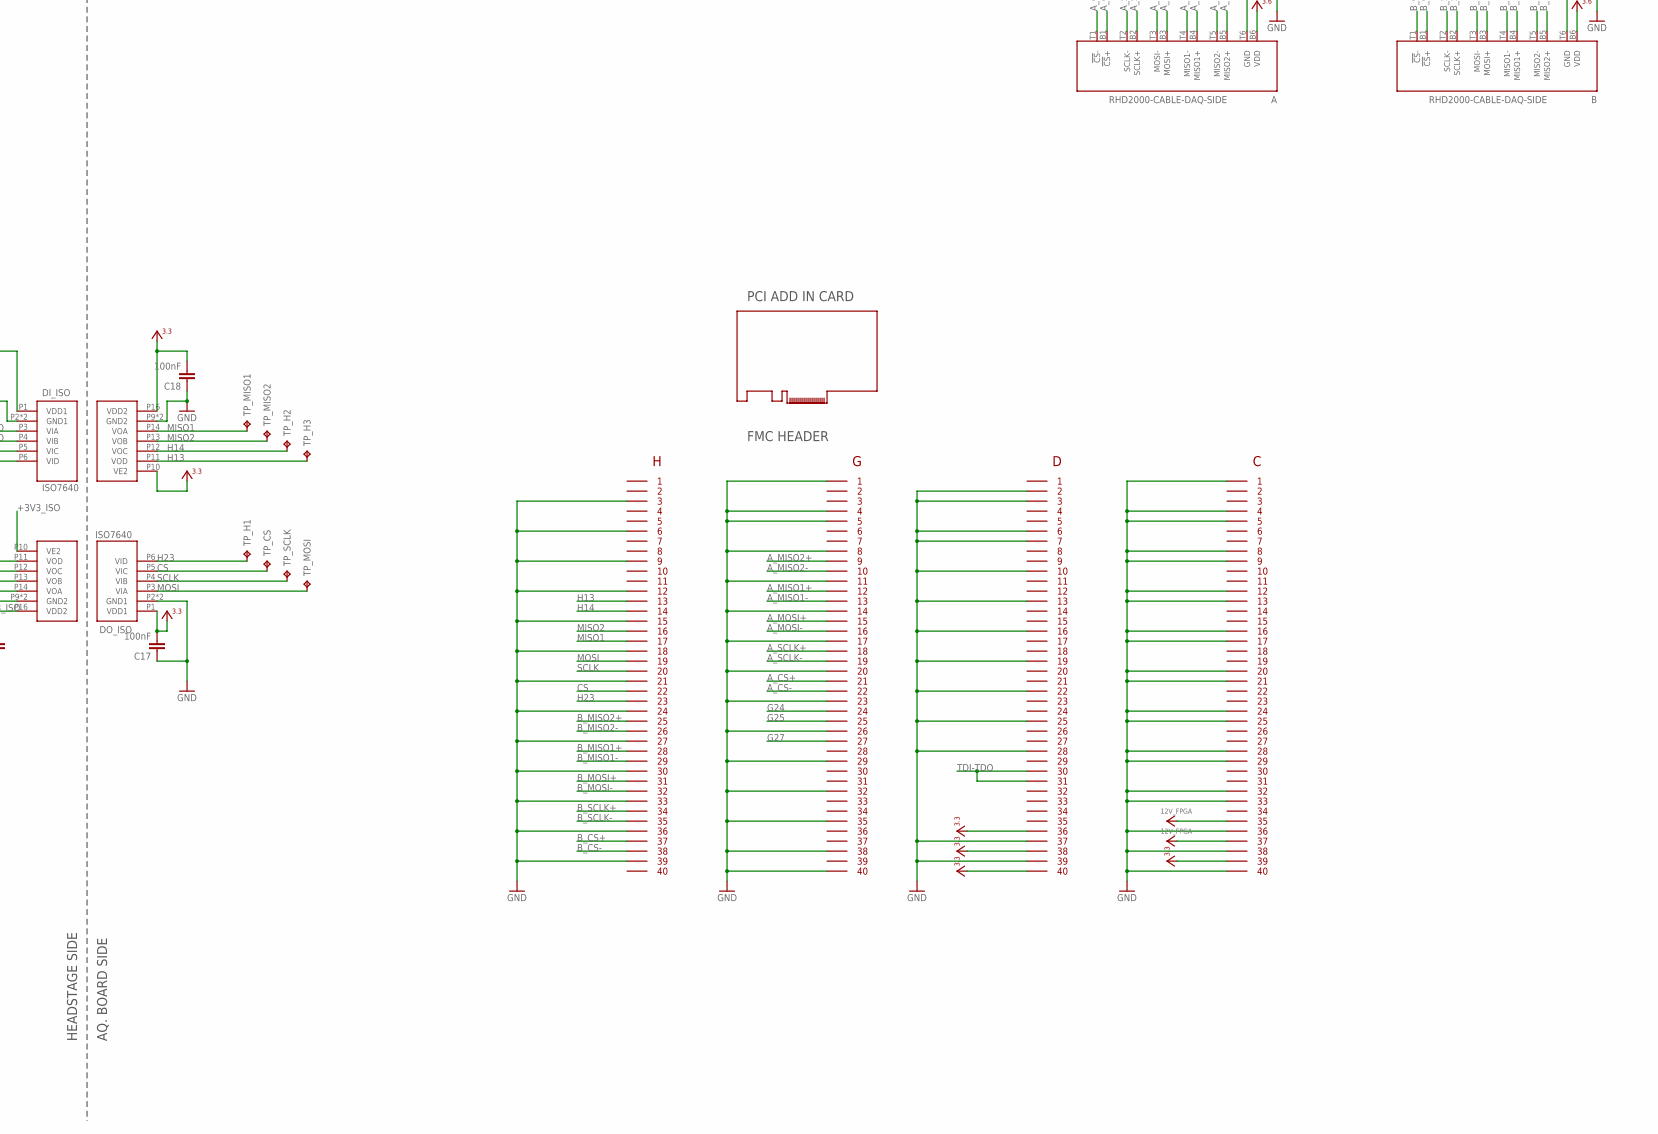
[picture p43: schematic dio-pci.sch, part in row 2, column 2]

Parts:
A: RHD2000-CABLE-DAQ-SIDE; OMNETICS_PZN-12-AA
B: RHD2000-CABLE-DAQ-SIDE; OMNETICS_PZN-12-AA
C1, C12, C13, C20, C24: 10uF; 1206
C2, C7, C22, C23: 10nF; 0603
C3: 22uF; 1206
C4, C5: 10uF; 1206-POL
C6, C33, C34, C35, C36, C37: 0.1uF; 0603
C8, C9, C10, C15, C16, C17, C18, C25, C27, C29, C30, C31, C32: 100nF; 0603
C11, C21: 1nF; 0603
C19: 2.2uF; 1206
C26, C28: 22uF; 1210-POL
C_ISO: RHD2000-CABLE-DAQ-SIDE; OMNETICS_PZN-12-AA
D1, D2, D3, D4, D5, D6, D7, D8: STPS0560Z; SOD123
D9: KDZ4.3B; SOD123
DI0, DI1: SMA002; SMA_JACK_CONREVSMA002-G
DI_ISO: ISO7640; SOIC_WIDE_16
DO0, DO1: SMA002; SMA_JACK_CONREVSMA002-G
DO_ISO: ISO7640; SOIC_WIDE_16
F1, F2, F3, F4: C014F-2; 1812
FMC: FMC_LPC_160_PIN; FMC_LPC_MALE_WITH_SP601_BSILK
IC1: AZ1117CH-3.3; SOT223
L1, L2, L3, L4: MPZ1608; 0603
L5: 82103C; 1210
POW_TP: JP3E; JP3
PWR_ISO: 569-011x; 569-011X-X00_LED_ARRAY
Q1, Q2: BSH103; SOT23-GSD
R1, R2, R3, R17, R18, R19: 150, 0.25W; 1206
R4, R7: 820; 0603
R5, R12: 20k; 0603
R6, R10, R13, R16, R23: 10k; 0603
R8, R9, R15, R22: 100; 0603
R11, R14, R20, R21, R24, R25, R26, R27: 2.2k; 0603
TP1: GND-ISO; P1-13
TP2: MOSI+; TP06R
TP3: SCLK+; TP06R
TP4: CS-; TP06R
TP5: MOSI-; TP06R
TP6: SCLK-; TP06R
TP7: CS+; TP06R
TP8, TP15: +5V0; TP06R
TP9: MISO2+; TP06R
TP10: +3V6; TP06R
TP11: MISO2-; TP06R
TP12: MISO1+; TP06R
TP13: +3V3; TP06R
TP14: MISO1-; TP06R
TP_CS: CS; TP06R
TP_H1: H23; TP06R
TP_H2: H14; TP06R
TP_H3: H13; TP06R
TP_MISO1: MISO1; TP06R
TP_MISO2: MISO2; TP06R
TP_MOSI: MOSI; TP06R
TP_SCLK: SCLK; TP06R
U1, U7: 4901; SOP65P490X110-9N
U3, U4: ADN4663; SOIC127P500X400-8N
U5: ADN4664; SOIC127P500X400-8N
U6: MEV3S1209SC; MEV3
U$1: OPEN_EPHYS_LOGO
U$2: PCI-MECH_STD-H_HALF-W; PCI-ADDIN_STD-H_HALF-L
U$5, U$6: ADCMP600; SOT-23-5
U$7: SN74LVT125; SO14

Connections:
12V_FPGA: C19.1, C26.+, C28.+, C30.2, C32.2, FMC.P$155, FMC.P$157, L5.1
$N1: D7.A, D8.C, F4.2, R17.2, R18.2, R19.2, R20.2, R22.1
$N3: D1.A, D2.C, F2.2, R1.2, R2.2, R3.2, R11.2, R15.1
$N101: D3.A, D4.C, F1.2, U$7.3 (1Y), U$7.6 (2Y)
$N102: D5.A, D6.C, F3.2, U$7.8 (3Y), U$7.11 (4Y)
+3V3: C17.2, C18.2, C25.2, C27.2, C29.2, C31.2, DI_ISO.P10 (VE2), DI_ISO.P16 (VDD2), DO_ISO.P1 (VDD1), FMC.P$116, FMC.P$118, FMC.P$120, FMC.P$159, POW_TP.1
+3V3_ISO: C3.1, C4.+, C5.+, C8.1, C9.1, C10.1, C15.2, C16.2, C35.2, C36.1, C37.1, DI_ISO.P1 (VDD1), DO_ISO.P10 (VE2), DO_ISO.P16 (VDD2), L4.2, R7.1, R24.2, R25.2, TP13.TP, U3.1 (VCC), U4.1 (VCC), U5.8 (VCC), U$5.5 (V+), U$6.5 (V+), U$7.14 (VCC)
+3V6: A.B6 (VDD), B.B6 (VDD), C23.1, C24.1, R12.1, U7.1 (OUT)
+3V6_ISO: C1.1, C2.1, C_ISO.B6 (VDD), R4.1, R5.1, TP10.TP, U1.1 (OUT)
+5V0: TP15.TP
+9V0_ISO: L1.1, L2.1, L3.1, R26.2, R27.2, U6.P4 (+VO)
AGND1: C23.2, R12.2, R13.1, U7.2 (FB)
AGND2: C2.2, R5.2, R6.1, U1.2 (FB)
A_CS+: A.B1 (!CS!+), FMC.P$61
A_CS-: A.T1 (!CS!-), FMC.P$62
A_MISO1+: A.B4 (MISO1+), FMC.P$52
A_MISO1-: A.T4 (MISO1-), FMC.P$53
A_MISO2+: A.B5 (MISO2+), FMC.P$49
A_MISO2-: A.T5 (MISO2-), FMC.P$50
A_MOSI+: A.B3 (MOSI+), FMC.P$55
A_MOSI-: A.T3 (MOSI-), FMC.P$56
A_SCLK+: A.B2 (SCLK+), FMC.P$58
A_SCLK-: A.T2 (SCLK-), FMC.P$59
BIAS_DI0: R16.1
BIAS_DI1: R23.1
B_CS+: B.B1 (!CS!+), FMC.P$37
B_CS-: B.T1 (!CS!-), FMC.P$38
B_MISO1+: B.B4 (MISO1+), FMC.P$28
B_MISO1-: B.T4 (MISO1-), FMC.P$29
B_MISO2+: B.B5 (MISO2+), FMC.P$25
B_MISO2-: B.T5 (MISO2-), FMC.P$26
B_MOSI+: B.B3 (MOSI+), FMC.P$31
B_MOSI-: B.T3 (MOSI-), FMC.P$32
B_SCLK+: B.B2 (SCLK+), FMC.P$34
B_SCLK-: B.T2 (SCLK-), FMC.P$35
CS: DO_ISO.P5 (VIC), FMC.P$22, TP_CS.TP
CS+_ISOLATED: C_ISO.B1 (!CS!+), TP7.TP, U4.7 (DOUT1+)
CS-_ISOLATED: C_ISO.T1 (!CS!-), TP4.TP, U4.8 (DOUT1-)
CS_ISO: DO_ISO.P12 (VOC), U4.2 (DIN1)
DI0_TERM_ISO: Q1.G, R14.2
DI1_TERM_ISO: Q2.G, R21.2
G24: FMC.P$64
G25: FMC.P$65
G27: FMC.P$67
GND: A.T6 (GND), B.T6 (GND), C17.1, C18.1, C19.2, C25.1, C26.-, C27.1, C28.-, C29.1, C30.1, C31.1, C32.1, DI_ISO.P9 (GND2), DI_ISO.P15 (GND2), DO_ISO.P2 (GND1), DO_ISO.P8 (GND1), FMC.GNDA (GND), FMC.GNDB (GND), FMC.P$3, FMC.P$6, FMC.P$9, FMC.P$12, FMC.P$15, FMC.P$18, FMC.P$21, FMC.P$24, FMC.P$27, FMC.P$30, FMC.P$33, FMC.P$36, FMC.P$39, FMC.P$41, FMC.P$44, FMC.P$45, FMC.P$48, FMC.P$51, FMC.P$54, FMC.P$57, FMC.P$60, FMC.P$63, FMC.P$66, FMC.P$69, FMC.P$72, FMC.P$75, FMC.P$78, FMC.P$80, FMC.P$82, FMC.P$83, FMC.P$86, FMC.P$87, FMC.P$90, FMC.P$93, FMC.P$96, FMC.P$99, FMC.P$102, FMC.P$105, FMC.P$108, FMC.P$117, FMC.P$119, FMC.P$121, FMC.P$124, FMC.P$125, FMC.P$128, FMC.P$129, FMC.P$132, FMC.P$133, FMC.P$136, FMC.P$137, FMC.P$140, FMC.P$141, FMC.P$144, FMC.P$145, FMC.P$148, FMC.P$149, FMC.P$152, FMC.P$153, FMC.P$156, FMC.P$158, FMC.P$160, POW_TP.3, U6.P2 (GND)
GND_ISO: C1.2, C3.2, C4.-, C5.-, C6.1, C7.2, C8.2, C9.2, C10.2, C11.2, C12.2, C13.2, C15.1, C16.1, C20.2, C21.2, C22.2, C24.2, C33.2, C34.2, C35.1, C36.2, C37.2, C_ISO.T6 (GND), D2.A, D4.A, D6.A, D8.A, D9.A, DI0.GND$1 (2), DI0.GND$2 (2), DI0.GND$3 (2), DI0.GND$4 (2), DI1.GND$1 (2), DI1.GND$2 (2), DI1.GND$3 (2), DI1.GND$4 (2), DI_ISO.P2 (GND1), DI_ISO.P8 (GND1), DO0.GND$1 (2), DO0.GND$2 (2), DO0.GND$3 (2), DO0.GND$4 (2), DO1.GND$1 (2), DO1.GND$2 (2), DO1.GND$3 (2), DO1.GND$4 (2), DO_ISO.P9 (GND2), DO_ISO.P15 (GND2), IC1.1 (ADJ), PWR_ISO.C1 (C), PWR_ISO.C2 (C), Q1.S, Q2.S, R6.2, R10.1, R11.1, R13.2, R14.1, R20.1, R21.1, TP1.TP, U1.4 (GND), U1.9 (EP), U3.4 (GND), U4.4 (GND), U5.5 (GND), U6.P3 (0V), U7.4 (GND), U7.9 (EP), U$5.2 (V-), U$6.2 (V-), U$7.7 (GND)
H13: DI_ISO.P11 (VOD), FMC.P$13, TP_H3.TP
H13_ISO: DI_ISO.P6 (VID), U$7.9 (3A), U$7.12 (4A)
H14: DI_ISO.P12 (VOC), FMC.P$14, TP_H2.TP
H14_ISO: DI_ISO.P5 (VIC), U$7.2 (1A), U$7.5 (2A)
H23: DO_ISO.P6 (VID), FMC.P$23, TP_H1.TP
H23_ISO: DO_ISO.P11 (VOD), U$5.1 (OUT)
MISO1: DI_ISO.P14 (VOA), FMC.P$17, TP_MISO1.TP
MISO1+_ISOLATED: C_ISO.B4 (MISO1+), R9.1, TP12.TP, U5.2 (RIN1+)
MISO1-_ISOLATED: C_ISO.T4 (MISO1-), R9.2, TP14.TP, U5.1 (RIN1-)
MISO1_ISO: DI_ISO.P3 (VIA), U5.7 (ROUT1)
MISO2: DI_ISO.P13 (VOB), FMC.P$16, TP_MISO2.TP
MISO2+_ISOLATED: C_ISO.B5 (MISO2+), R8.1, TP9.TP, U5.3 (RIN2+)
MISO2-_ISOLATED: C_ISO.T5 (MISO2-), R8.2, TP11.TP, U5.4 (RIN2-)
MISO2_ISO: DI_ISO.P4 (VIB), U5.6 (ROUT2)
MOSI: DO_ISO.P3 (VIA), FMC.P$19, TP_MOSI.TP
MOSI_ISO: DO_ISO.P14 (VOA), U3.2 (DIN1)
unnamed: C22.1, U7.6 (NR/SS)
unnamed: Q1.D, R1.1, R2.1, R3.1
unnamed: R15.2, U$5.3 (+IN)
unnamed: C7.1, U1.6 (NR/SS)
unnamed: R10.2, U4.3 (DIN2)
unnamed: DI1.CLK (1), F4.1
unnamed: Q2.D, R17.1, R18.1, R19.1
unnamed: PWR_ISO.A2 (A), R4.2
unnamed: C11.1, C12.1, L1.2, U1.5 (EN), U1.8 (IN)
unnamed: PWR_ISO.A1 (A), R7.2
unnamed: DI0.CLK (1), F2.1
unnamed: C_ISO.B3 (MOSI+), TP2.TP, U3.7 (DOUT1+)
unnamed: C_ISO.T3 (MOSI-), TP5.TP, U3.8 (DOUT1-)
unnamed: DO0.CLK (1), F1.1
unnamed: C_ISO.B2 (SCLK+), TP3.TP, U3.6 (DOUT2+)
unnamed: C_ISO.T2 (SCLK-), TP6.TP, U3.5 (DOUT2-)
unnamed: DO1.CLK (1), F3.1
unnamed: C33.1, R16.2, U$5.4 (-IN)
unnamed: R22.2, U$6.3 (+IN)
unnamed: C34.1, R23.2, U$6.4 (-IN)
unnamed: C13.1, IC1.4 (VO), L3.2
unnamed: IC1.3 (VI), L4.1
unnamed: L5.2, U6.P1 (VIN)
unnamed: R24.1, U$7.1 (~1G), U$7.4 (~2G)
unnamed: R25.1, U$7.10 (~3G), U$7.13 (~4G)
SCLK: DO_ISO.P4 (VIB), FMC.P$20, TP_SCLK.TP
SCLK_ISO: DO_ISO.P13 (VOB), U3.3 (DIN2)
SOMEWHERE_ISO: U$6.1 (OUT)
TDI-TDO: FMC.P$110, FMC.P$111
VDD_POST_LC: C20.1, C21.1, L2.2, U7.5 (EN), U7.8 (IN)
V_PROTECT: C6.2, D1.C, D3.C, D5.C, D7.C, D9.C, R26.1, R27.1, TP8.TP

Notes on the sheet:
HEADSTAGE SIDE
AQ. BOARD SIDE
Isolated 3.3V reg.
3.6V regulator for RHD TODO: Each RHD has a regulator
12V-TO-9V ISOLATED DC-DC
ISOLATED PWR TEST POINTS
NOMINAL PWR TEST POINTS
GALVANICALLY ISOLATED SPI BUS
FMC HEADER
PCI ADD IN CARD
TODO: - DAC to set LL bias on comparitors
V_PROTECT ~4.6V

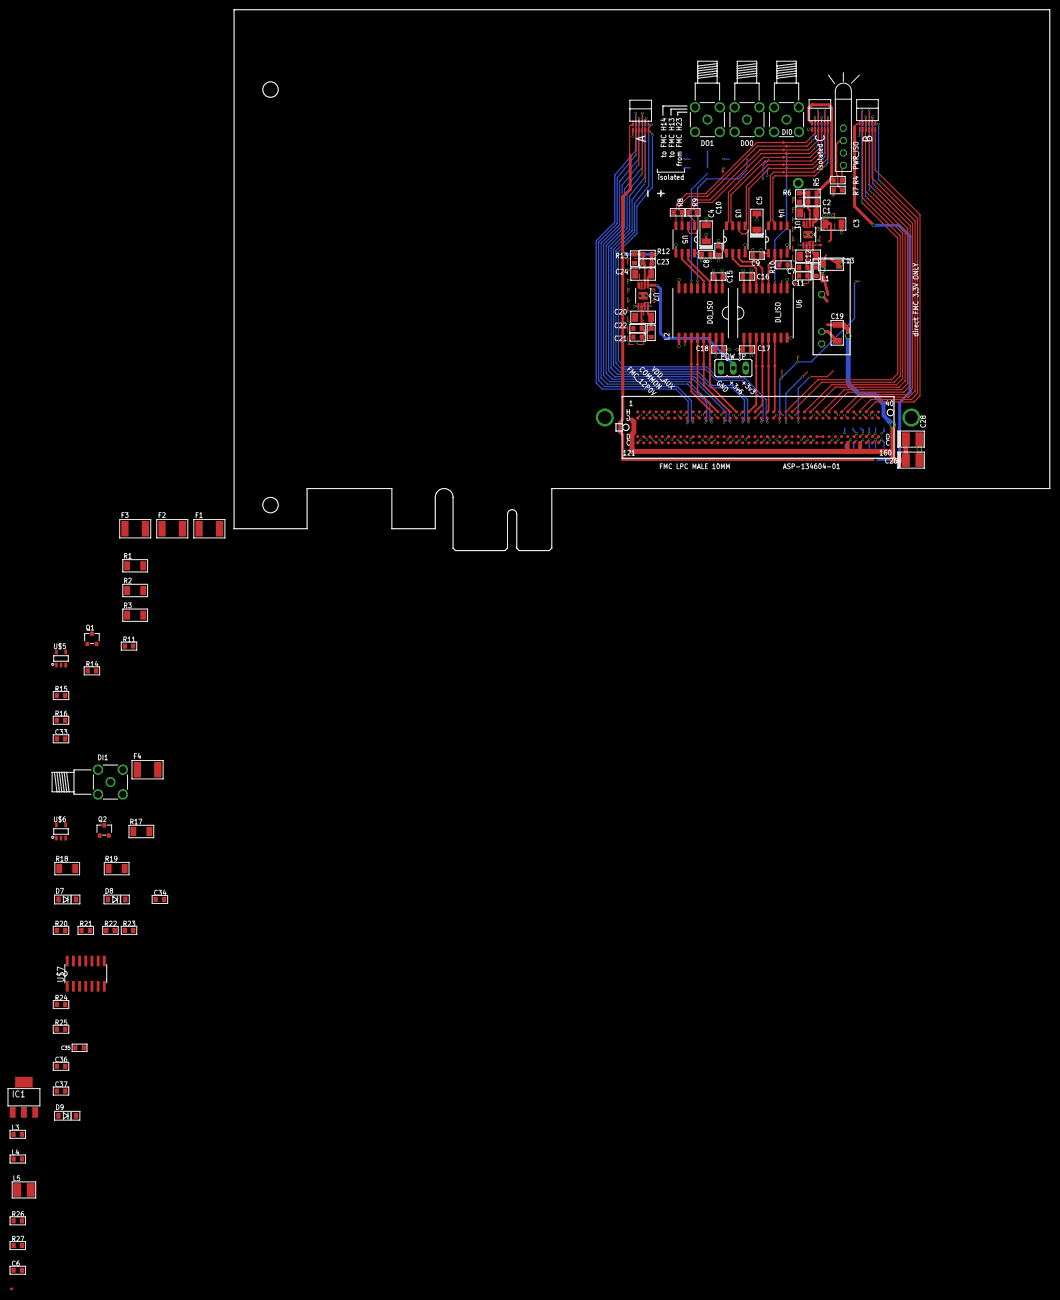
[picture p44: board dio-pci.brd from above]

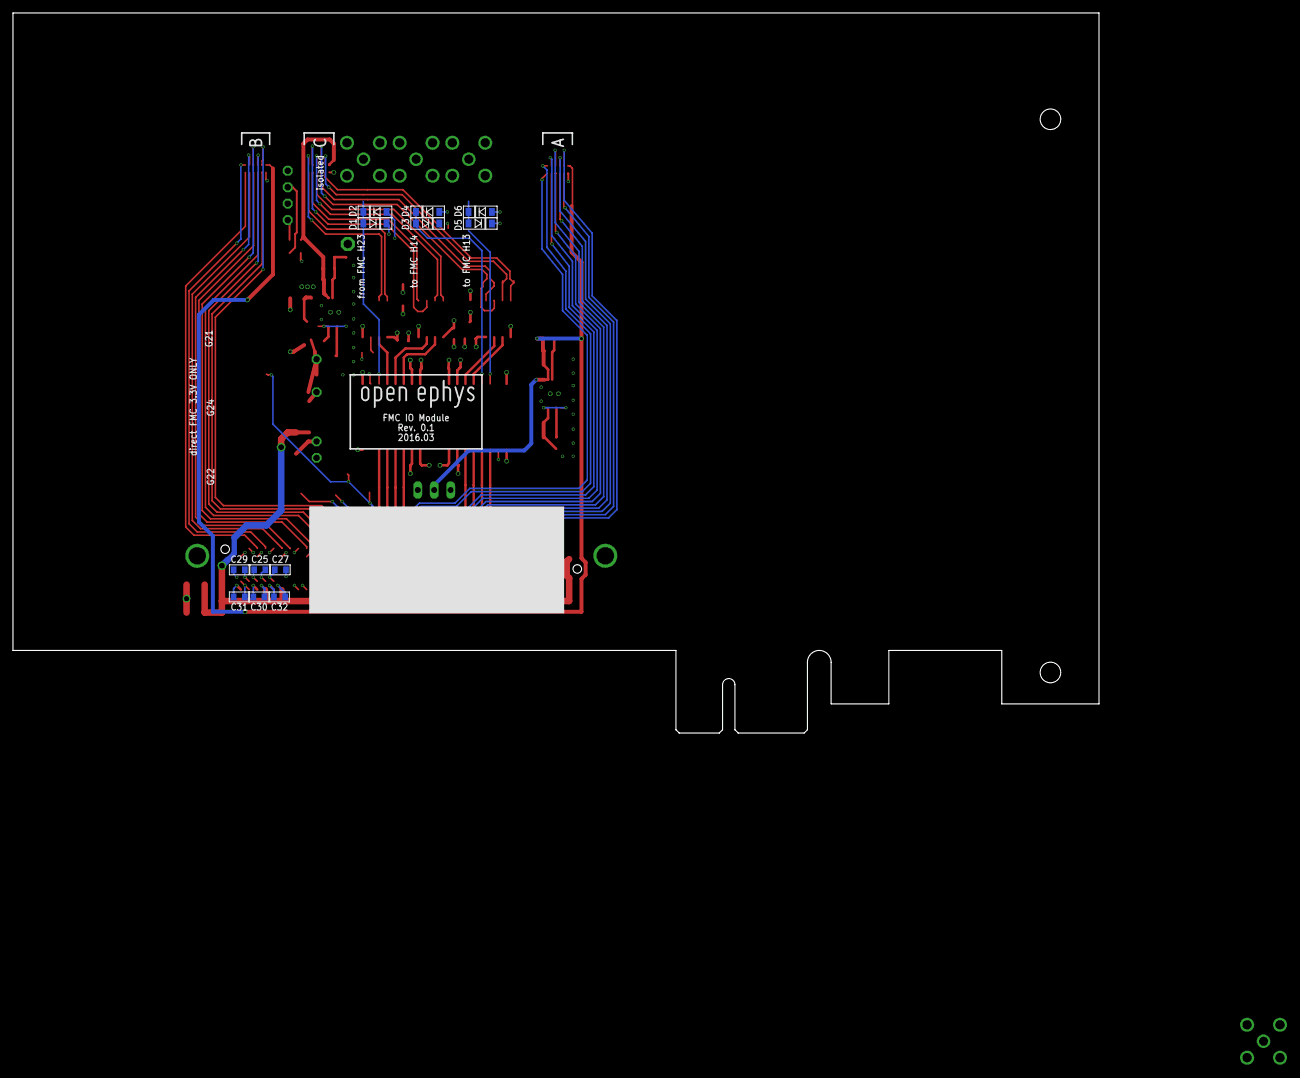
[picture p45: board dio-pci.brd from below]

Board: 4 copper layers, 167.6 x 111.2 mm, 130 parts (14 on the bottom side), 86 nets.

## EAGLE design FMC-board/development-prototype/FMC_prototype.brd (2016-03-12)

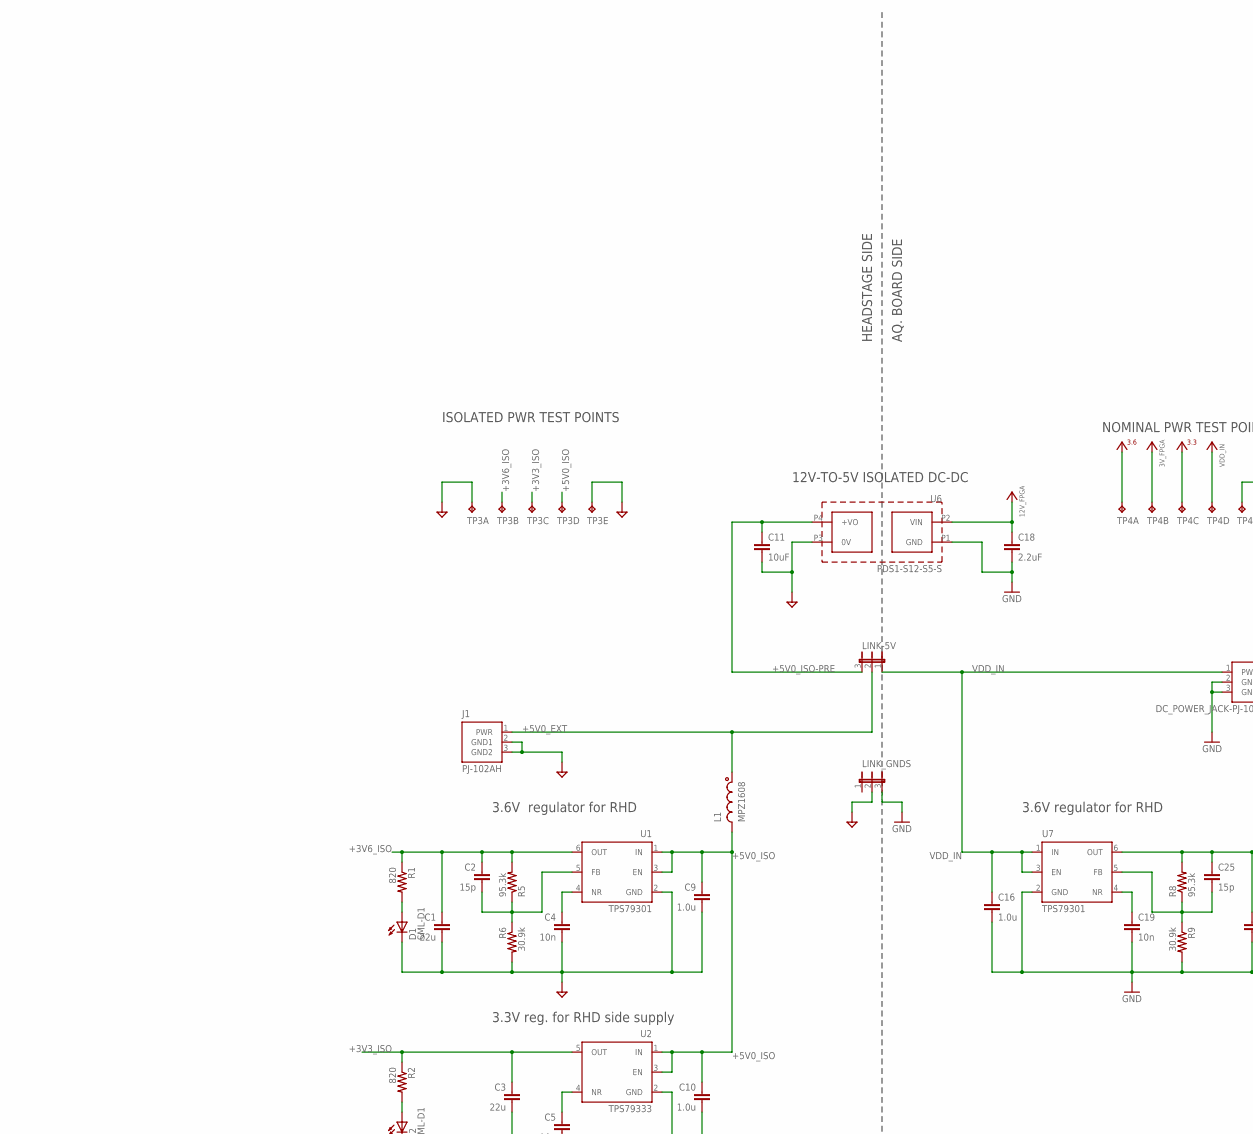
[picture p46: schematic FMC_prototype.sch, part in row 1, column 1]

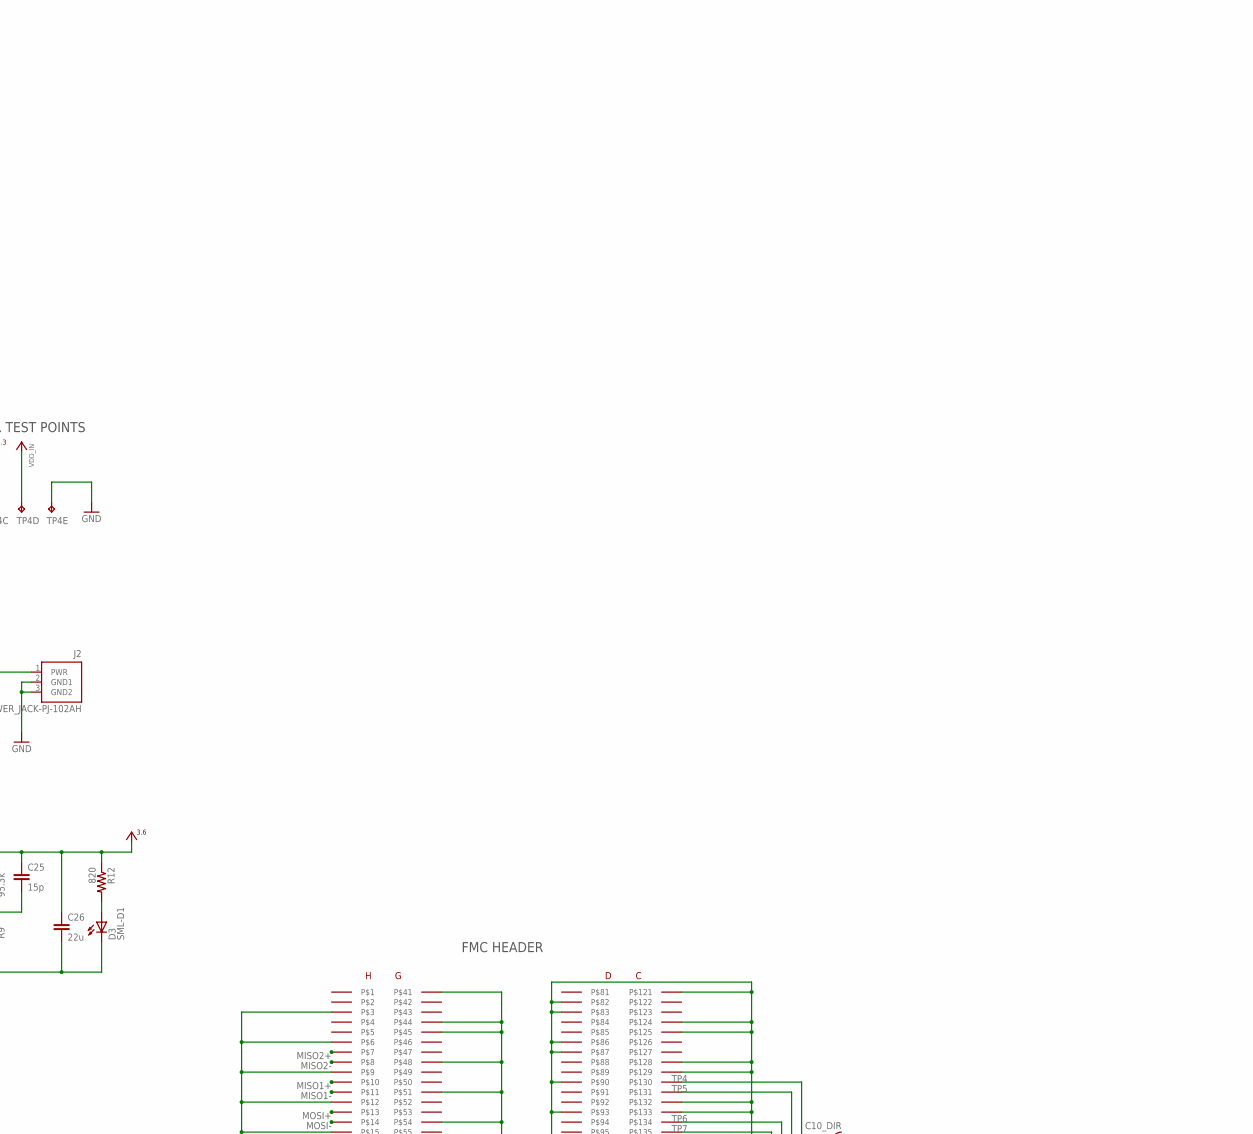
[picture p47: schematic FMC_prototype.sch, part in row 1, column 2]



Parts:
A: RHD2000-CABLE-DAQ-SIDE; OMNETICS_PZN-12-AA
A_ISOLATED: RHD2000-CABLE-DAQ-SIDE; OMNETICS_PZN-12-AA
B: RHD2000-CABLE-DAQ-SIDE; OMNETICS_PZN-12-AA
C1, C3, C26: 22u; 1206
C2, C25: 15p; 0603
C4, C5, C19: 10n; 0603
C6, C7, C8, C12, C13, C14, C15, C21, C22, C23: 100n; 0603
C9, C10, C16: 1.0u; 0805
C10_DIR, C11_DIR, C14_DIR, C15_DIR, C18_DIR: 142-0701; SMA_JACK_142-0701-201
C11: 10uF; 1206
C18: 2.2uF; 1206
D1, D2, D3: SML-D1; LED-0603
DI_ISO: ISO7640; SOIC_WIDE_16
DO_ISO: IS07640; SOIC_WIDE_16
FMC: FMC_LPC_160_PIN; FMC_LPC_MALE_WITH_SP601_BSILK
G22_ISO: 142-0701; SMA_JACK_142-0701-201
H21_ISO, H22_ISO: 142-0701; SMA_JACK_142-0701-201
J1: PJ-102AH
J2: DC_POWER_JACK-PJ-102AH; PJ-102AH
L1: MPZ1608; 0603
LINK-5V: JP2E; JP2
LINK_GNDS: JP2E; JP2
R1, R2, R12: 820; 0603
R3, R4: 100; 0603
R5, R8: 95.3k; 0603
R6, R9: 30.9k; 0603
R7, R10, R11: 10k; 0603
R14, R15, R16, R17, R18, R19, R20, R21, R22, R23: 0; 0603
TP1, TP2, TP3, TP4, TP5: TP5P5-25-13; P5-25-13
U1, U7: TPS79301; SOT-23-6
U2: TPS79333; SOT-23-5
U3, U4, U11: ADN4663; SOIC127P500X400-8N
U5, U9, U10: ADN4664; SOIC127P500X400-8N
U6: PDS1-S12-S5-S; PDS1
U$1: OPEN_EPHYS_LOGO

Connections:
12V_FPGA: C18.1, FMC.P$155, FMC.P$157, U6.P2 (VIN)
+3V3: C14.2, C15.2, C21.1, C22.1, C23.1, DI_ISO.P10 (VE2), DI_ISO.P16 (VDD2), DO_ISO.P1 (VDD1), FMC.P$116, FMC.P$118, FMC.P$120, FMC.P$159, TP4.TP-2, TP4.TP-3, U9.8 (VCC), U10.8 (VCC), U11.1 (VCC)
+3V3_ISO: C3.1, C6.1, C7.1, C8.1, C12.2, C13.2, DI_ISO.P1 (VDD1), DO_ISO.P10 (VE2), DO_ISO.P16 (VDD2), R2.1, TP3.TP-3, U2.5 (OUT), U3.1 (VCC), U4.1 (VCC), U5.8 (VCC)
+3V6: A.B6 (VDD), B.B6 (VDD), C25.1, C26.1, R8.2, R12.1, TP4.TP-1, U7.6 (OUT)
+3V6_ISO: A_ISOLATED.B6 (VDD), C1.1, C2.1, R1.1, R5.2, TP3.TP-2, U1.6 (OUT)
+5V0_EXT: J1.1 (PWR), L1.1, LINK-5V.2
+5V0_ISO: C9.1, C10.1, L1.2, TP3.TP-4, U1.1 (IN), U1.3 (EN), U2.1 (IN), U2.3 (EN)
+5V0_ISO-PRE: C11.1, LINK-5V.3, U6.P4 (+VO)
A_CS+: A.B1 (!CS!+), R15.1
A_CS-: A.T1 (!CS!-), R14.1
A_MISO1+: A.B4 (MISO1+), R21.1
A_MISO1-: A.T4 (MISO1-), R20.1
A_MISO2+: A.B5 (MISO2+), R23.1
A_MISO2-: A.T5 (MISO2-), R22.1
A_MOSI+: A.B3 (MOSI+), R19.1
A_MOSI-: A.T3 (MOSI-), R18.1
A_SCLK+: A.B2 (SCLK+), R17.1
A_SCLK-: A.T2 (SCLK-), R16.1
B_CS+: B.B1 (!CS!+), FMC.P$37, TP5.TP-1
B_CS-: B.T1 (!CS!-), FMC.P$38
B_MISO1+: B.B4 (MISO1+), FMC.P$28, TP5.TP-4
B_MISO1-: B.T4 (MISO1-), FMC.P$29
B_MISO2+: B.B5 (MISO2+), FMC.P$25, TP5.TP-5
B_MISO2-: B.T5 (MISO2-), FMC.P$26
B_MOSI+: B.B3 (MOSI+), FMC.P$31, TP5.TP-3
B_MOSI-: B.T3 (MOSI-), FMC.P$32
B_SCLK+: B.B2 (SCLK+), FMC.P$34, TP5.TP-2
B_SCLK-: B.T2 (SCLK-), FMC.P$35
CS+: FMC.P$19, R15.2, U10.2 (RIN1+)
CS+_ISOLATED: A_ISOLATED.B1 (!CS!+), U4.7 (DOUT1+)
CS-: FMC.P$20, R14.2, U10.1 (RIN1-)
CS-_ISOLATED: A_ISOLATED.T1 (!CS!-), U4.8 (DOUT1-)
CS_ISOLATED_SE: DO_ISO.P13 (VOB), U4.2 (DIN1)
CS_SE: DO_ISO.P4 (VIB), U10.7 (ROUT1)
GND: A.T6 (GND), B.T6 (GND), C10_DIR.GND$1 (2), C10_DIR.GND$2 (2), C10_DIR.GND$3 (2), C10_DIR.GND$4 (2), C11_DIR.GND$1 (2), C11_DIR.GND$2 (2), C11_DIR.GND$3 (2), C11_DIR.GND$4 (2), C14.1, C14_DIR.GND$1 (2), C14_DIR.GND$2 (2), C14_DIR.GND$3 (2), C14_DIR.GND$4 (2), C15.1, C15_DIR.GND$1 (2), C15_DIR.GND$2 (2), C15_DIR.GND$3 (2), C15_DIR.GND$4 (2), C16.2, C18.2, C18_DIR.GND$1 (2), C18_DIR.GND$2 (2), C18_DIR.GND$3 (2), C18_DIR.GND$4 (2), C19.2, C21.2, C22.2, C23.2, C26.2, D3.C, DI_ISO.P9 (GND2), DI_ISO.P15 (GND2), DO_ISO.P2 (GND1), DO_ISO.P8 (GND1), FMC.GNDA (GND), FMC.GNDB (GND), FMC.P$3, FMC.P$6, FMC.P$9, FMC.P$12, FMC.P$15, FMC.P$18, FMC.P$21, FMC.P$24, FMC.P$27, FMC.P$30, FMC.P$33, FMC.P$36, FMC.P$39, FMC.P$41, FMC.P$44, FMC.P$45, FMC.P$48, FMC.P$51, FMC.P$54, FMC.P$57, FMC.P$60, FMC.P$63, FMC.P$66, FMC.P$69, FMC.P$72, FMC.P$75, FMC.P$78, FMC.P$80, FMC.P$82, FMC.P$83, FMC.P$86, FMC.P$87, FMC.P$90, FMC.P$93, FMC.P$96, FMC.P$99, FMC.P$102, FMC.P$105, FMC.P$108, FMC.P$117, FMC.P$119, FMC.P$121, FMC.P$124, FMC.P$125, FMC.P$128, FMC.P$129, FMC.P$132, FMC.P$133, FMC.P$136, FMC.P$137, FMC.P$140, FMC.P$141, FMC.P$144, FMC.P$145, FMC.P$148, FMC.P$149, FMC.P$152, FMC.P$153, FMC.P$156, FMC.P$158, FMC.P$160, J2.2 (GND1), J2.3 (GND2), LINK_GNDS.3, R9.2, R10.1, R11.1, TP2.TP-5, TP4.TP-5, U6.P1 (GND), U7.2 (GND), U9.5 (GND), U10.5 (GND), U11.4 (GND)
GND_ISO: A_ISOLATED.T6 (GND), C1.2, C3.2, C4.2, C5.2, C6.2, C7.2, C8.2, C9.2, C10.2, C11.2, C12.1, C13.1, D1.C, D2.C, DI_ISO.P2 (GND1), DI_ISO.P8 (GND1), DO_ISO.P9 (GND2), DO_ISO.P15 (GND2), G22_ISO.GND$1 (2), G22_ISO.GND$2 (2), G22_ISO.GND$3 (2), G22_ISO.GND$4 (2), H21_ISO.GND$1 (2), H21_ISO.GND$2 (2), H21_ISO.GND$3 (2), H21_ISO.GND$4 (2), H22_ISO.GND$1 (2), H22_ISO.GND$2 (2), H22_ISO.GND$3 (2), H22_ISO.GND$4 (2), J1.2 (GND1), J1.3 (GND2), LINK_GNDS.2, R6.2, R7.1, TP1.TP-1, TP3.TP-1, TP3.TP-5, U1.2 (GND), U2.2 (GND), U3.4 (GND), U4.4 (GND), U5.5 (GND), U6.P3 (0V)
MISO1+: FMC.P$10, R21.2, TP2.TP-2, U11.6 (DOUT2+)
MISO1+_ISOLATED: A_ISOLATED.B4 (MISO1+), R4.1, TP1.TP-4, U5.3 (RIN2+)
MISO1-: FMC.P$11, R20.2, U11.5 (DOUT2-)
MISO1-_ISOLATED: A_ISOLATED.T4 (MISO1-), R4.2, U5.4 (RIN2-)
MISO1_ISOLATED_SE: DI_ISO.P4 (VIB), TP1.TP-5, U5.6 (ROUT2)
MISO1_SE: DI_ISO.P13 (VOB), TP2.TP-1, U11.3 (DIN2)
MISO2+: FMC.P$7, R23.2, U11.7 (DOUT1+)
MISO2+_ISOLATED: A_ISOLATED.B5 (MISO2+), R3.1, U5.2 (RIN1+)
MISO2-: FMC.P$8, R22.2, U11.8 (DOUT1-)
MISO2-_ISOLATED: A_ISOLATED.T5 (MISO2-), R3.2, U5.1 (RIN1-)
MISO2_ISOLATED_SE: DI_ISO.P3 (VIA), U5.7 (ROUT1)
MISO2_SE: DI_ISO.P14 (VOA), U11.2 (DIN1)
MOSI+: FMC.P$13, R19.2, TP2.TP-4, U9.3 (RIN2+)
MOSI+_ISOLATED: A_ISOLATED.B3 (MOSI+), TP1.TP-2, U3.6 (DOUT2+)
MOSI-: FMC.P$14, R18.2, U9.4 (RIN2-)
MOSI-_ISOLATED: A_ISOLATED.T3 (MOSI-), U3.5 (DOUT2-)
MOSI_ISOLATED_SE: DO_ISO.P11 (VOD), TP1.TP-3, U3.3 (DIN2)
MOSI_SE: DO_ISO.P6 (VID), TP2.TP-3, U9.6 (ROUT2)
unnamed: R11.2, U10.3 (RIN2+)
unnamed: R10.2, U10.4 (RIN2-)
unnamed: D3.A, R12.2
unnamed: R7.2, U4.3 (DIN2)
unnamed: D2.A, R2.2
unnamed: D1.A, R1.2
unnamed: C19.1, U7.4 (NR)
unnamed: C25.2, R8.1, R9.1, U7.5 (FB)
unnamed: C4.1, U1.4 (NR)
unnamed: C2.2, R5.1, R6.1, U1.5 (FB)
unnamed: C5.1, U2.4 (NR)
SCLK+: FMC.P$16, R17.2, U9.2 (RIN1+)
SCLK+_ISOLATED: A_ISOLATED.B2 (SCLK+), U3.7 (DOUT1+)
SCLK-: FMC.P$17, R16.2, U9.1 (RIN1-)
SCLK-_ISOLATED: A_ISOLATED.T2 (SCLK-), U3.8 (DOUT1-)
SCLK_ISOLATED_SE: DO_ISO.P12 (VOC), U3.2 (DIN1)
SCLK_SE: DO_ISO.P5 (VIC), U9.7 (ROUT1)
TP1_FROM_SMA: DI_ISO.P5 (VIC), H21_ISO.CLK (1)
TP1_TO_FPGA: DI_ISO.P12 (VOC), FMC.P$22
TP2_FROM_SMA: DI_ISO.P6 (VID), H22_ISO.CLK (1)
TP2_TO_FPGA: DI_ISO.P11 (VOD), FMC.P$23
TP3_FROM_FPGA: DO_ISO.P3 (VIA), FMC.P$62
TP3_TO_SMA: DO_ISO.P14 (VOA), G22_ISO.CLK (1)
TP4: C10_DIR.CLK (1), FMC.P$130
TP5: C11_DIR.CLK (1), FMC.P$131
TP6: C14_DIR.CLK (1), FMC.P$134
TP7: C15_DIR.CLK (1), FMC.P$135
TP8: C18_DIR.CLK (1), FMC.P$138
VDD_IN: C16.1, J2.1 (PWR), LINK-5V.1, TP4.TP-4, U7.1 (IN), U7.3 (EN)

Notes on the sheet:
HEADSTAGE SIDE
AQ. BOARD SIDE
3.3V reg. for RHD side supply
3.6V regulator for RHD
12V-TO-5V ISOLATED DC-DC
ISOLATED PWR TEST POINTS
NOMINAL PWR TEST POINTS
3.6V regulator for RHD
GALVANICALLY ISOLATED SPI BUS
FMC HEADER


Board: 4 copper layers, 103.9 x 69.8 mm, 84 parts (0 on the bottom side), 83 nets.

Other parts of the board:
U$16: INTAN_LOGO

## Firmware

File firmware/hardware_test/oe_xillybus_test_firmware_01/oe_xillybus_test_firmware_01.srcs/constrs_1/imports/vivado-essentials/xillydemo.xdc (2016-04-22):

# START AUTO-GENERATED BY XILLYBUS
create_clock -name sys_clk -period 10 [get_pins -match_style ucf */pcieclk_ibuf/O]

set_false_path -to [get_pins -match_style ucf */pipe_clock/pclk_i1_bufgctrl.pclk_i1/S0]
set_false_path -to [get_pins -match_style ucf */pipe_clock/pclk_i1_bufgctrl.pclk_i1/S1]
set_case_analysis 1 [get_pins -match_style ucf */pipe_clock/pclk_i1_bufgctrl.pclk_i1/S0]
set_case_analysis 0 [get_pins -match_style ucf */pipe_clock/pclk_i1_bufgctrl.pclk_i1/S1]

set_property DONT_TOUCH true [get_cells -of [get_nets -of [get_pins -match_style ucf */pipe_clock/pclk_i1_bufgctrl.pclk_i1/S0]]]
set_property DONT_TOUCH true [get_cells -hier -filter {name=~*/pipe_clock/pclk_sel*}]

set_false_path -from [get_ports PCIE_PERST_B_LS]

set_property LOC IBUFDS_GTE2_X0Y1 [get_cells -match_style ucf */pcieclk_ibuf]

set_property -dict "PACKAGE_PIN G25 IOSTANDARD LVCMOS25 PULLUP true" [get_ports PCIE_PERST_B_LS]

set_property -dict "PACKAGE_PIN AB8 IOSTANDARD LVCMOS15" [get_ports "GPIO_LED[0]"]
set_property -dict "PACKAGE_PIN AA8 IOSTANDARD LVCMOS15" [get_ports "GPIO_LED[1]"]
set_property -dict "PACKAGE_PIN AC9 IOSTANDARD LVCMOS15" [get_ports "GPIO_LED[2]"]
set_property -dict "PACKAGE_PIN AB9 IOSTANDARD LVCMOS15" [get_ports "GPIO_LED[3]"]
# END AUTO-GENERATED BY XILLYBUS

# isolated output from FPGA 
set_property PACKAGE_PIN AK26 [get_ports sma_out_isol_H23]
set_property IOSTANDARD LVCMOS33 [get_ports sma_out_isol_H23]

# isolated inputs to FPGA 
set_property PACKAGE_PIN AG25 [get_ports sma_in_isol_H13]
set_property IOSTANDARD LVCMOS33 [get_ports sma_in_isol_H13]

set_property PACKAGE_PIN AH25 [get_ports sma_in_isol_H14]
set_property IOSTANDARD LVCMOS33 [get_ports sma_in_isol_H14]

# direct SMAs (G24, 25, 27)
set_property PACKAGE_PIN AJ27 [get_ports sma_direct_G24]
set_property IOSTANDARD LVCMOS33 [get_ports sma_direct_G24] 

set_property PACKAGE_PIN AK28 [get_ports sma_direct_G25]
set_property IOSTANDARD LVCMOS33 [get_ports sma_direct_G25] 

set_property PACKAGE_PIN AC26 [get_ports sma_direct_G27]
set_property IOSTANDARD LVCMOS33 [get_ports sma_direct_G27] 


# C spi port (isolated, simple cmos33 logic, gets translated to lvds after isolator)
set_property PACKAGE_PIN AE25 [get_ports MISO_C1]
set_property IOSTANDARD LVCMOS33 [get_ports MISO_C1]

set_property PACKAGE_PIN AF25 [get_ports MISO_C2]
set_property IOSTANDARD LVCMOS33 [get_ports MISO_C2]

set_property PACKAGE_PIN AC24 [get_ports MOSI_C]
set_property IOSTANDARD LVCMOS33 [get_ports MOSI_C]

set_property PACKAGE_PIN AD24 [get_ports SCLK_C]
set_property IOSTANDARD LVCMOS33 [get_ports SCLK_C]

set_property PACKAGE_PIN AJ26 [get_ports CS_C]
set_property IOSTANDARD LVCMOS33 [get_ports CS_C]

# TODO: If we want to acctually use the isolated SPI busses, we need to make sure they use
# the same VCCO as the singled ended ports on the same bank. If they need to use a different
# VCCO, then their DIFF_TERM property should be set to false. Ideally, we should not have any
# non isolated pins anyway, so this is probably all mute.

## B spi port (non-isolated, goes straight to FMC pins)
#set_property PACKAGE_PIN AG30 [get_ports MISO_B1_p]
#set_property PACKAGE_PIN AH30 [get_ports MISO_B1_n]
#set_property IOSTANDARD LVDS_25 [get_ports {MISO_B1_p MISO_B1_n}]

#set_property PACKAGE_PIN AG27 [get_ports MISO_B2_p]
#set_property PACKAGE_PIN AG28 [get_ports MISO_B2_n]
#set_property IOSTANDARD LVDS_25 [get_ports {MISO_B2_p MISO_B2_n}]

#set_property PACKAGE_PIN AE30 [get_ports MOSI_B_p]
#set_property PACKAGE_PIN AF30 [get_ports MOSI_B_n]
#set_property IOSTANDARD LVDS_25 [get_ports {MOSI_B_p MOSI_B_n}]

#set_property PACKAGE_PIN AB29 [get_ports SCLK_B_p]
#set_property PACKAGE_PIN AB30 [get_ports SCLK_B_n]
#set_property IOSTANDARD LVDS_25 [get_ports {SCLK_B_p SCLK_B_n}]

#set_property PACKAGE_PIN Y30 [get_ports CS_B_p]
#set_property PACKAGE_PIN AA30 [get_ports CS_B_n]
#set_property IOSTANDARD LVDS_25 [get_ports {CS_B_p CS_B_n}]

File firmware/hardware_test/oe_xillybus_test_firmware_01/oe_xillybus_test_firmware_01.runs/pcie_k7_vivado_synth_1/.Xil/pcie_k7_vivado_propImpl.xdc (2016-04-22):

set_property SRC_FILE_INFO {cfile:/home/oe/Downloads/xillybus-eval-kintex7-1.2d/vivado-essentials/pcie_k7_vivado/source/pcie_k7_vivado-PCIE_X0Y0.xdc rfile:../../../../../vivado-essentials/pcie_k7_vivado/source/pcie_k7_vivado-PCIE_X0Y0.xdc id:1 order:EARLY scoped_inst:inst} [current_design]
set_property src_info {type:SCOPED_XDC file:1 line:79 export:INPUT save:INPUT read:READ} [current_design]
set_property LOC GTXE2_CHANNEL_X0Y7 [get_cells {inst/gt_top_i/pipe_wrapper_i/pipe_lane[0].gt_wrapper_i/gtx_channel.gtxe2_channel_i}]
set_property src_info {type:SCOPED_XDC file:1 line:81 export:INPUT save:INPUT read:READ} [current_design]
set_property LOC GTXE2_CHANNEL_X0Y6 [get_cells {inst/gt_top_i/pipe_wrapper_i/pipe_lane[1].gt_wrapper_i/gtx_channel.gtxe2_channel_i}]
set_property src_info {type:SCOPED_XDC file:1 line:83 export:INPUT save:INPUT read:READ} [current_design]
set_property LOC GTXE2_CHANNEL_X0Y5 [get_cells {inst/gt_top_i/pipe_wrapper_i/pipe_lane[2].gt_wrapper_i/gtx_channel.gtxe2_channel_i}]
set_property src_info {type:SCOPED_XDC file:1 line:85 export:INPUT save:INPUT read:READ} [current_design]
set_property LOC GTXE2_CHANNEL_X0Y4 [get_cells {inst/gt_top_i/pipe_wrapper_i/pipe_lane[3].gt_wrapper_i/gtx_channel.gtxe2_channel_i}]
set_property src_info {type:SCOPED_XDC file:1 line:87 export:INPUT save:INPUT read:READ} [current_design]
set_property LOC GTXE2_CHANNEL_X0Y3 [get_cells {inst/gt_top_i/pipe_wrapper_i/pipe_lane[4].gt_wrapper_i/gtx_channel.gtxe2_channel_i}]
set_property src_info {type:SCOPED_XDC file:1 line:89 export:INPUT save:INPUT read:READ} [current_design]
set_property LOC GTXE2_CHANNEL_X0Y2 [get_cells {inst/gt_top_i/pipe_wrapper_i/pipe_lane[5].gt_wrapper_i/gtx_channel.gtxe2_channel_i}]
set_property src_info {type:SCOPED_XDC file:1 line:91 export:INPUT save:INPUT read:READ} [current_design]
set_property LOC GTXE2_CHANNEL_X0Y1 [get_cells {inst/gt_top_i/pipe_wrapper_i/pipe_lane[6].gt_wrapper_i/gtx_channel.gtxe2_channel_i}]
set_property src_info {type:SCOPED_XDC file:1 line:93 export:INPUT save:INPUT read:READ} [current_design]
set_property LOC GTXE2_CHANNEL_X0Y0 [get_cells {inst/gt_top_i/pipe_wrapper_i/pipe_lane[7].gt_wrapper_i/gtx_channel.gtxe2_channel_i}]
set_property src_info {type:SCOPED_XDC file:1 line:101 export:INPUT save:INPUT read:READ} [current_design]
set_property LOC PCIE_X0Y0 [get_cells inst/pcie_top_i/pcie_7x_i/pcie_block_i]
set_property src_info {type:SCOPED_XDC file:1 line:106 export:INPUT save:INPUT read:READ} [current_design]
set_property LOC RAMB36_X5Y35 [get_cells {inst/pcie_top_i/pcie_7x_i/pcie_bram_top/pcie_brams_rx/brams[3].ram/use_tdp.ramb36/genblk*.bram36_tdp_bl.bram36_tdp_bl}]
set_property src_info {type:SCOPED_XDC file:1 line:107 export:INPUT save:INPUT read:READ} [current_design]
set_property LOC RAMB36_X4Y36 [get_cells {inst/pcie_top_i/pcie_7x_i/pcie_bram_top/pcie_brams_rx/brams[2].ram/use_tdp.ramb36/genblk*.bram36_tdp_bl.bram36_tdp_bl}]
set_property src_info {type:SCOPED_XDC file:1 line:108 export:INPUT save:INPUT read:READ} [current_design]
set_property LOC RAMB36_X4Y35 [get_cells {inst/pcie_top_i/pcie_7x_i/pcie_bram_top/pcie_brams_rx/brams[1].ram/use_tdp.ramb36/genblk*.bram36_tdp_bl.bram36_tdp_bl}]
set_property src_info {type:SCOPED_XDC file:1 line:109 export:INPUT save:INPUT read:READ} [current_design]
set_property LOC RAMB36_X4Y34 [get_cells {inst/pcie_top_i/pcie_7x_i/pcie_bram_top/pcie_brams_rx/brams[0].ram/use_tdp.ramb36/genblk*.bram36_tdp_bl.bram36_tdp_bl}]
set_property src_info {type:SCOPED_XDC file:1 line:110 export:INPUT save:INPUT read:READ} [current_design]
set_property LOC RAMB36_X4Y33 [get_cells {inst/pcie_top_i/pcie_7x_i/pcie_bram_top/pcie_brams_tx/brams[0].ram/use_tdp.ramb36/genblk*.bram36_tdp_bl.bram36_tdp_bl}]
set_property src_info {type:SCOPED_XDC file:1 line:111 export:INPUT save:INPUT read:READ} [current_design]
set_property LOC RAMB36_X4Y32 [get_cells {inst/pcie_top_i/pcie_7x_i/pcie_bram_top/pcie_brams_tx/brams[1].ram/use_tdp.ramb36/genblk*.bram36_tdp_bl.bram36_tdp_bl}]
set_property src_info {type:SCOPED_XDC file:1 line:112 export:INPUT save:INPUT read:READ} [current_design]
set_property LOC RAMB36_X4Y31 [get_cells {inst/pcie_top_i/pcie_7x_i/pcie_bram_top/pcie_brams_tx/brams[2].ram/use_tdp.ramb36/genblk*.bram36_tdp_bl.bram36_tdp_bl}]
set_property src_info {type:SCOPED_XDC file:1 line:113 export:INPUT save:INPUT read:READ} [current_design]
set_property LOC RAMB36_X4Y30 [get_cells {inst/pcie_top_i/pcie_7x_i/pcie_bram_top/pcie_brams_tx/brams[3].ram/use_tdp.ramb36/genblk*.bram36_tdp_bl.bram36_tdp_bl}]

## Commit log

2016-02-25 added copy of isolation board
    might be useful to work from, or see if there's already a verified design for this
    [headstage_isolation_board_01.brd, headstage_isolation_board_01.sch]
2016-02-26 Initial commit FMC board prototype
    this is pretty much just a wiped version of the board from
    http://www.ohwr.org/projects/lpcfmc12pexp/files
    Still need to verify everything on this, then figure out the
    dimensions, pinout etc. and then start adding in things
    [FMC_prototype.brd, FMC_prototype.sch]
2016-02-28 added basic isolator circuitry sch
    [FMC_prototype.brd, FMC_prototype.sch]
2016-02-28 initial board layout fpga side
    [FMC_prototype.brd, FMC_prototype.sch]
2016-02-28 initial layout isolated section
    [FMC_prototype.brd]
2016-02-28 more placement and labels
    [FMC_prototype.brd, FMC_prototype.sch]
2016-02-28 more power layout
    started adding pins on the LPC FMC connector
    [FMC_prototype.brd, FMC_prototype.sch]
2016-02-29 added 3.6V regulator for non-isolated SPI connectors
    [FMC_prototype.brd, FMC_prototype.sch]
2016-02-29 started adding SPI signals for A
    still not routed
    [FMC_prototype.brd, FMC_prototype.sch]
2016-02-29 routed nonisolated A SPI connector
    [FMC_prototype.brd]
2016-02-29 connected B SPI
    [FMC_prototype.brd]
2016-02-29 routed B SPI connector
    [FMC_prototype.brd, FMC_prototype.sch]
2016-02-29 small cleanups
    [FMC_prototype.brd]
2016-03-01 more small cleanups
    [FMC_prototype.brd]
2016-03-01 added measurement points (just+) to all B connector LVDS signals
    [FMC_prototype.brd, FMC_prototype.sch]
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2016-03-04 added proper ground plane
    this is now 4 layers but its somewhat cleaner this way
    [FMC_prototype.brd]
2016-03-04 added testpoints
    still some unrouted parts
    [FMC_prototype.brd, FMC_prototype.sch]
2016-03-04 routed isolated testpoints
    likely still errors in there
    [FMC_prototype.brd]
2016-03-04 more cleanup
    [FMC_prototype.brd]
2016-03-05 cleanup, starting DRC
    [FMC_prototype.brd]
2016-03-05 clearing all but layer setup and silkscreen overlap warnings
    [FMC_prototype.brd, FMC_prototype.sch]
2016-03-05 added spreadsheet of pinout diagram
    same as https://docs.google.com/spreadsheets/d/1bgnBP1xqPFtFIQYF-BCybK1KkekfmRYwm2GDAU4D9lo/edit?usp=sharing
    [next gen ephys system HMC LPC pinout.ods]
2016-03-06 added optional DC DC converter
    12V > 5V DC DC for powering headstage etc. can still be bypassed with jumper
    [FMC_prototype.brd, FMC_prototype.sch]
2016-03-06 Fixed small routing error on DC DC converter
    [FMC_prototype.brd]
2016-03-07 More or less done checking power section of schematic.
    [FMC_prototype.brd, FMC_prototype.sch]
2016-03-07 Started working on digital ports.
    [FMC_prototype.brd, FMC_prototype.sch]
2016-03-07 Cleaning up schematic as a means to understand and verify it.
    [FMC_prototype.brd, FMC_prototype.sch]
2016-03-07 Looks like isolated 5V was wired to output of isolated 3.6V regulator and input is floating to both isolated regulators. In the middle of fixing that.
    [FMC_prototype.brd, FMC_prototype.sch]
2016-03-07 More digital port cleanup.
    [FMC_prototype.brd, FMC_prototype.sch]
2016-03-08 Almost done with my revisions to schematic. Need to go through ERC.
    [FMC_prototype.brd, FMC_prototype.sch]
2016-03-08 Fixed reversed polarity on LVDS drvr/recv's.
    [FMC_prototype.brd, FMC_prototype.sch]
2016-03-08 Almost ready to merge with master. Needs a couple more ERC checks.
    [FMC_prototype.brd, FMC_prototype.sch]
2016-03-08 Finished updating the schematic
    - TODOs moved to the FMC board's README.md rather than the top level
    one.
    - Need to verify that the dev board supports internal LVDS termination
    [FMC_prototype.brd, FMC_prototype.sch]
2016-03-08 Minor cleanups.
    [FMC_prototype.brd, FMC_prototype.sch]
2016-03-08 rough layout
    [FMC_prototype.brd, FMC_prototype.sch]
2016-03-08 more layout
    [FMC_prototype.brd]
2016-03-09 layout mostly cleaned up now
    still needs proper DRC, probably ERC and almost all labels etc need to
    be fixed
    [FMC_prototype.brd]
2016-03-09 small layout fixes
    [FMC_prototype.brd]
2016-03-09 improved B headstage routing
    no more branches going to test points
    [FMC_prototype.brd]
2016-03-12 fixed some name and value labels
    [FMC_prototype.brd]
2016-03-12 added labels to testpoints
    [FMC_prototype.brd]
2016-03-12 Reworking power planes and differential signal routing
    - Removed top/bottom ground planes.
    - High speed signal ended signals: return current flows beneath trace
    - Differential signals: avoid large loop areas. Ideally, trances should
    be parallel until they terminate on a pad or through characteristic
    impedance.
    - The large test points are problematic. I really think we should
    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
    [FMC_prototype.brd, FMC_prototype.sch]
2016-03-12 Changes to differential pair layout and power
    - Mostly finished with non-isolated side.
    - Moved decoupling caps closer to target ICs and provided low impedance
    paths to ground power
    - Differential traces wired together
    - Got rid of non-isolated side 3.3V regulator because there is just no
    reason non to use the FMC 3.3V rail -- if that does not work, then the
    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
    [FMC_prototype.brd, FMC_prototype.sch]
2016-03-13 Toward meeting fmc standards
    - I read the VITA 57.1 standard and I think it would be worth it to make
    the board marginally compliant (even on first run) because it is not
    very dense and this really will inform the future design of the board
    - Also, it will make it compatible with 100's of carrier boards with all
    sorts of FPGAs and DSPs onboard
    [FMC_prototype.brd, FMC_prototype.sch]
2016-03-13 Toward VITA-57.1 compliance
    - Found pad alignment issues in the SOIC16 digital isolation chips.
    Fixed that.
    - Layout changes informed by VITA 57.1 and several FMC modules designed
    by CERN for data collection in high-energy physics experiments.
    - Removed power jacks for now. Replaced with simple headers and reverse
    polarity protection to make up for the automatic polarity protection
    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
    [FMC_prototype.brd, FMC_prototype.sch]
2016-03-13 About 50% through routing
    - The FMC<->Driver/Reciver<->Isolator<->Driver/Receiver path needs to be
    rearranged to minimize crossovers
    [FMC_prototype.brd, FMC_prototype.sch]
2016-03-14 Removed FPGA side LVDS drivers/receivers
    - Not needed as all FMC connections can be configured as single
    ended
    - Started BOM
    - Switched to RA SMAs on the panel side of board
    [FMC_prototype.brd, FMC_prototype.sch]
2016-03-14 Lots of routing simplification
    - Moved non-isolated SPI buses onto there own IO on the FMC connector
    since there is plenty of that. Got rid of the branches and jumper
    resistors as a result.
    - Only a bit more wiring todo before be ERC/DRC stage.
    [FMC_prototype.brd, FMC_prototype.sch]
2016-03-14 More routing.
    [FMC_prototype.brd, FMC_prototype.sch]
2016-03-15 Nearly finished with routing, try to finish tonight.
    [FMC_prototype.brd, FMC_prototype.sch]
2016-03-15 Hard routing complete
    - Inner SMAs need hookups
    - Should bezel be tied to GND_ISO?
    - Re-add testpoints (pad style)
    - Silkscreen...
    [FMC_prototype.brd, FMC_prototype.sch]
2016-03-15 Done with initial routing of FMC-compliant board
    - Get others to examine before messing with silkscreen a putting in test
    points.
    [FMC_prototype.brd, FMC_prototype.sch]
2016-03-15 Cleanup. Added images of schematic/board.
    [FMC_prototype.brd, FMC_prototype.sch, headstage_isolation_board_01.brd, headstage_isolation_board_01.sch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]
2016-03-16 tightened routing a bit & added 3v3 test point
    [FMC_prototype.brd, FMC_prototype.sch]
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2016-03-17 More silkscreen fixes and test points
    - Added test pads for digital lines on paths through isolation
    circuitry. Used small inline padsto prevent stubs.
    - Silkscreen looks pretty good now.
    - Boards needs a fresh look over then fab, I think.
    [FMC_prototype.brd, FMC_prototype.sch]
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2016-03-18 Fixed SMA component names to match new FMC loctaions.
    [FMC_prototype.brd, FMC_prototype.sch]
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2016-04-24 Isolated DIO input circuit design on dio-pic card
    - Replace current limit resistors with fast polyfuse with I_trip <
    schottky I_max sustained
    - Optional 50 Ohm termination on input SMAs
    - TTL Logic-level tolerant line driver on output SMAs
    - Programable logic level on input SMAs. Still needs DAC on isolated
    side to set bias voltages
    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
    [dio-pci.brd, dio-pci.sch]
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2016-11-17 initial commit of spacing test for FMC card for 8 intan SPI connectors
    looks a whole lot like the isolators won;t fit - may have to switch to a smaller package on these and accept a lower isolation standard
    [FMC_intan_RHD_interface.brd, FMC_intan_RHD_interface.sch]
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

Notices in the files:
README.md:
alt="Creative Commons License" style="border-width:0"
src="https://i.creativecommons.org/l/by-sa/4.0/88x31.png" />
